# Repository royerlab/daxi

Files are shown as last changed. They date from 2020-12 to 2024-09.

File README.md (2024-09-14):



# DaXi: High-Resolution, Large Imaging Volume, and Multi-View Single Objective Light-Sheet Microscope

DaXi_blender_render

The DaXi microscope is a single-objective light-sheet microscope design that combines the advantages of standard single-objective microscopes with the speed, coverage, resolution, and gentleness of light-sheet microscopes. Its main features include a wider field of view and high-resolution imaging via a custom remote focusing objective, fast volumetric imaging over larger volumes without compromising image quality or necessitating tiled acquisition, fuller image coverage for large samples via multi-view imaging, and higher throughput multi-well imaging via remote coverslip placement. The microscope achieves a resolution of 450 nm laterally and 2 μm axially over an imaging volume of 3,000 × 800 × 300 μm, making it suitable for imaging large living samples such as developing embryos. The DaXi microscope also improves sample mounting ergonomics and can be converted from upright to inverted using remote focusing. The microscope has been successfully used to image various systems, including Drosophila egg chamber development, zebrafish whole-brain activity, and zebrafish embryonic development, up to nine embryos at a time.

DaXi has been published in Nature Methods in 2022:
[Yang, B., Lange, M., Millett-Sikking, A. et al. DaXi—high-resolution, large imaging volume and multi-view single-objective light-sheet microscopy. Nat Methods 19, 461–469 (2022).](https://doi.org/10.1038/s41592-022-01417-2)

Biorxiv preprint: https://doi.org/10.1101/2020.09.22.309229
Suplementary information for the paper can be found [here](https://www.biorxiv.org/content/10.1101/2020.09.22.309229v2.supplementary-material).  

This repository contains all CAD drawings, parts list, control software, and simulation for the microscope.
It is our goal to enable the community to build their own replicates of this system. Don't hesitate to post 
issues to this repo to request addtional information or report issues.  

Correspondence: loic.royer@czbiohub.org, bin.yang@czbiohub.org

## Contents

* [CAD models](https://github.com/royerlab/daxi/tree/master/cad_models): custom designed parts used to built the microscope. The STL files can be used directly 
for 3D printing.

* [Part list](https://github.com/royerlab/daxi/tree/master/part_list): a list of all the necessary parts used to built the microscope. 
A rough estimate of the cost of the microscope is about $130k.

* [Control code](https://github.com/royerlab/daxi/tree/master/control_code): to control the microscope. A Micro-Manager script to setup the data acquisition and 
a python module to programme a NI DAQ system to synchronize other devices during the acquisition. 
Micro-Manager is used to control the camera and the microscope stage. 
The NI DAQ system uses digital signal to switch the lasers on/off, and analog signals to set the angle of
the galvo mirrors and the position of the piezo actuators. 

* [Simulation code](https://github.com/royerlab/daxi/tree/master/simulation_code): used to generate the results in Supplementary Figures 7 and 9. 

## Image Processing

The image processing code required to go from DaXi's raw data to a fully processed timelapse or even video is found [here](https://github.com/royerlab/dexp).

## Software Requirements
Code is only tested on Windows 10 operating system, many hardware drivers only exist for windows...

Micro-Manager Version is 2.0-gamma.

Python version 3.7.

## Citation:

If you use the hardwar designs or software code, please cite us:

[High-Resolution, Large Imaging Volume, and Multi-View Single Objective Light-Sheet Microscopy](https://doi.org/10.1101/2020.09.22.309229)

Bin Yang1*, Merlin Lange, Alfred Millett-Sikking, Ahmet Can Solak, Shruthi Vijaykumar, Wanpeng Wang, 
Hirofumi Kobayashi, Matthew N Mccarroll, Lachlan W Whitehead, Reto P Fiolka, Thomas B. Kornberg, 
Andrew G York, Loic A. Royer*

Link to the Biorxiv preprint:  https://doi.org/10.1101/2020.09.22.309229

## License
This project is covered under the BSD 3-clause license.

Copyright © 2021. Chan Zuckerberg Biohub. All rights reserved.



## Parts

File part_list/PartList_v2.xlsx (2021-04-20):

 |  |  |  |  | Grand total | $130568.35 | Prices don’t include tax
Optics in Figure
Utility | Decription | Supplier | Part number | Unit Price | Quantity | Sub_total | Note
O1 | 1.0NA 20x water objective | Olympus | XLUMPLFLN 20XW | $7189.00 | 1 | $7189.00
O2 | 0.80NA 20x air objective | Olympus | UPLXAPO20X | $3075.00 | 1 | $3075.00
O3 | 1.0NA 20x Solid Immersion | Special Optics | Calico AMS 2.0 | $30000.00 | 1 | $30000.00 | Custom objective from Calico, price is estimated
Scanning and swtiching galvos | 20 mm Galvo mirror, 40 Degree Optical Angle, S4 mirror | Cambridge Instrument | 6SD12205 | $2567.00 | 3 | $7701.00 | see Miscellenous for galvo control | need custom mount
2-axes galvo | galvo to adjust incident angles of the light sheet | Cambridge Instrument | 6SD12056 | $6288.00 | 1 | $6288.00 | need custom mount to have true orthorgonal axes
Emission Filter | Single band filter | Chroma | ET525/50m | $325.00 | 1 | $325.00
Emission Filter | Single band filter | Chroma | ET610/75m | $325.00 | 1 | $325.00
Excitation Filter | Quad band filter | Chroma | 89402x | $550.00 | 1 | $550.00
Dichroic mirror | Quad band filter | Chroma | ZT405/488/561/640rpcv2-UF3 | $700.00 | 1 | $700.00
TL1-TL3 | Super wide tube lens | Olympus | SWTLU-C | $383.52 | 3 | $1150.56
TL4-TL6 components | Laser Scanning Tube Lens | Thorlabs | TTL200MP | $1379.17 | 3 | $4137.51
TL4-TL6 components | 2 inch achromatic lens | Thorlabs | AC508-750 | $112.54 | 2 | $225.08
TL4-TL6 components | 2 inch achromatic lens | Thorlabs | AC508-500 | $112.54 | 2 | $225.08
TL4-TL6 components | 2 inch achromatic lens | Thorlabs | AC508-750-A-ML | $148.25 | 2 | $296.50
TL7_alternative | Tube Lens, f = 200 mm, | Thorlabs | TTL200 | $496.70 | 1 | $496.70 | can be used to adjust final magnification
TL7_alternative | Tube Lens, f = 165 mm, | Thorlabs | TTL165A | $731.30 | 1 | $731.30 | can be used to adjust final magnification
TL7_alternative | Tube Lens, f = 100 mm | Thorlabs | TTL100A | $818.85 | 1 | $818.85 | can be used to adjust final magnification
CL1 | cylindrical lens 50 mm | Thorlabs | LJ1695RM-A | $109.29 | 1 | $109.29
CL2 and CL3 | cylindrical lens 200 mm | Thorlabs | LJ1653RM-A | $114.70 | 2 | $229.40
Fiber output | Protected Silver Reflective Collimator, 450 nm - 20 µm, Ø2 mm Beam, FC/APC | Thorlabs | RC02APCP01 | $966.34 | 1 | $966.34
Other major devices
Utility | Decription | Supplier | Part number | Unit Price | Quantity | Sub_total | Note
Piezo for O3 | Fast PIFOC® Piezo Nanofocusing Z-Drive, 100μm | Physik Instrumente | PD72Z1SAQ | $4946.00 | 1 | $4946.00 | Including the controller | not used in current setup yet
Laser | Stradus series module at 488nm, 50mW output with ~0.8 mm beam | Vortran | Stradus® 488 – 50 | $5240.00 | 1 | $5240.00
Laser | Stradus series module at 561nm, 50mW output with ~0.7 mm beam | Vortran | Stradus® 561 – 50 | $5364.00 | 1 | $5364.00
Data acquistion card | CompactDAQ chassis (8 slot USB) | National Instrument | cDAQ-9178 | $1443.00 | 1 | $1443.00
Data acquistion card | 4 Ch, +/-10 V, 16-Bit, 100 kS/s/ch, AO Module | National Instrument | NI 9263 DSUB | $564.00 | 2 | $1128.00
Data acquistion card | 8-Channel, 100 ns, TTL Digital Input/Output Module | National Instrument | NI 9401 | $341.00 | 1 | $341.00
Sample translation | MS-2000 FLAT-TOP XY AUTOMATED STAGE | ASI | MS-2000 | $12950.00 | 1 | $12950.00 | include controller and stage insert | Hindsight: need to include the scan-optimized option
Fiber input | FiberPort, FC/APC | Thorlabs | PAF2-A7A | $626.12 | 1 | $626.12
Miscellenous
Utility | Decription | Supplier | Part number | Unit Price | Quantity | Sub_total | Note
For galvos | HOOK-UP STRND 14AWG Wires for Galvo controller | Digikey | NA | $455.94 | 1 | $455.94
For galvos | SWITCHING POWER SUPPLIES | Astrodyne TDI | MK320S-24 | $83.11 | 6 | $498.66
Camera | ORCA-Flash4.0 V3 Digital | Hamamastu | C13440-20CU-KIT | $16500.00 | 1 | $16500.00
Camera | Interface Kit - Firebird Camlink Board and 2 ea SDR-SDR Caml | Hamamastu | CAMRA-1007-000-KIT | $2000.00 | 1 | $2000.00
Custom mounts
Utility | Decription | Supplier | Part number | Unit Price | Quantity | Sub_total | Note
For galvos | CambrigeGavloMount 2 axes, orthorgonal mount | Protolabs | NA | $842.90 | 1 | $842.90 | CAD file available
For O1 mount | ST1XY_PiezoAdapter_bottom | Protolabs | NA | $161.00 | 1 | $161.00 | CAD file available
For O1 mount | ST1XY_PiezoAdapter_top | Protolabs | NA | $155.76 | 1 | $155.76 | CAD file available
For O1 mount | XR25P_Piezo_adapter_bottom | Protolabs | NA | $171.94 | 1 | $171.94 | CAD file available
For O1 mount | XR25P_Piezo_adapter_top | Protolabs | NA | $174.00 | 1 | $174.00 | CAD file available
For galvos | 20mmGalvoMount - Part 1_v2, custom mount | Protolabs | NA | $335.45 | 3 | $1006.35 | CAD file available
For O1 water dispenser | Olympus1p00_20x - ObjectiveWaterDispenser | 3D-printed | NA | NA | 1 | NA | CAD file available
Thorlabs optomechanics
O1-O3 translation | Manual translation stages | Thorlabs | XR25P | $436.09 | 3 | $1308.27
O1 translation | Motorized translation stages | Thorlabs | ZFS25B (https://www.thorlabs.com/thorproduct.cfm?partnumber=ZFS25B) | $1250.92 | 1 | $1250.92
xy translation | XY Translator with Micrometer Drives | Thorlabs | ST1XY-S | $400.38 | 4 | $1601.52 | for objectives and fiberoutput
Mirror mount | Right-Angle Kinematic Mirror Mount | Thorlabs | KCB2C | $173.99 | 4 | $695.96
Mirror mount | Right-Angle Kinematic Mirror Mount | Thorlabs | KCB1C | $147.29 | 4 | $589.16
Mirror mount | Polaris® Ø2" Mirror Mount | Thorlabs | POLARIS-K2 | $293.25 | 3 | $879.75
Cage system | 60 mm Cage Plate, SM2 Threads | Thorlabs | LCP01 | $41.12 | 3 | $123.36
Alignment reference | PostMountable Standard Iris, Ø20.0 mm Max Aperture | Thorlabs | IDA20P5 | $223.78 | 1 | $223.78
Alignement check | Positive Combined Resolution and Distortion Test Target | Thorlabs | R1L1S1P | $520.05 | 1 | $520.05
Olympus tube lens adpator | Modified SM2-Threaded Mounting Adapter | Thorlabs | SM2AD-M41-SP | $120.00 | 3 | $360.00
Post | Ø1" Pedestal Pillar Post | Thorlabs | RS2P8E | $25.97 | 6 | $155.82
Post | Ø1" Post Holder with Flexure Lock, Pedestal Base | Thorlabs | RSH1.5 (https://www.thorlabs.com/thorproduct.cfm?partnumber=RSH1.5) | $33.28 | 2 | $66.56
Post | Ø1" Pillar Post | Thorlabs | RS1.5 | $23.27 | 2 | $46.54
Mirror mount | Compact Kinematic Mirror Mount Hex Adjuster | Thorlabs | KMSS | $37.87 | 3 | $113.61 | for dual view switch
Translation stage | Compact†25†mm†Travel†Linear†Translation†Stage | Thorlabs | XRN25C | $427.54 | 1 | $427.54 | for dual view switch
Translation stage | Baseplate†for†Stages†with†2¢†Wide†Dovetails | Thorlabs | XRNB1 | $32.62 | 1 | $32.62 | for dual view switch
Breadboard assembly | Aluminum Breadboard | Thorlabs | MB8 | $74.90 | 1 | $74.90 | parts to assemble the breadboard
Breadboard assembly | Aluminum Breadboard | Thorlabs | MB1218 | $187.83 | 1 | $187.83 | parts to assemble the breadboard
Breadboard assembly | Aluminum Breadboard | Thorlabs | MB618 | $129.11 | 1 | $129.11 | parts to assemble the breadboard
Breadboard assembly | Aluminum Breadboard | Thorlabs | MB1824 | $375.66 | 1 | $375.66 | parts to assemble the breadboard
Breadboard assembly | Aluminum Breadboard | Thorlabs | MB1836 | $568.64 | 1 | $568.64 | parts to assemble the breadboard
Breadboard assembly | Aluminum Breadboard | Thorlabs | MB810 | $115.16 | 1 | $115.16 | parts to assemble the breadboard
Breadboard assembly | Right≠Angle†Mounting†Plate | Thorlabs | AP90 | $83.71 | 3 | $251.13 | parts to assemble the breadboard
Breadboard assembly | Large Right-Angle Mounting Plate | Thorlabs | AP90L | $164.27 | 1 | $164.27 | parts to assemble the breadboard
Breadboard assembly | 18" Vertical Bracket for Breadboards | Thorlabs | VB01B | $129.11 | 3 | $387.33 | parts to assemble the breadboard
Dichroic mount | Kinematic†Fluorescence†Filter†Cube¨ | Thorlabs | DFM1L | $374.58 | 1 | $374.58

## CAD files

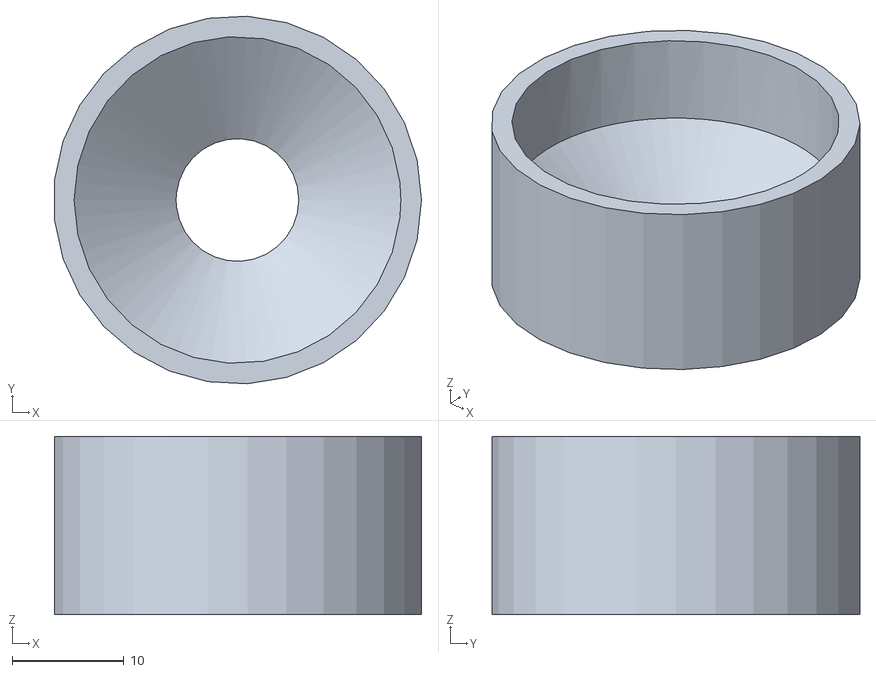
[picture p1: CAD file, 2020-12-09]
cad_models/Olympus1p00_20x - ObjectiveWaterDispenser.stl
32.9 x 33.0 x 16.0

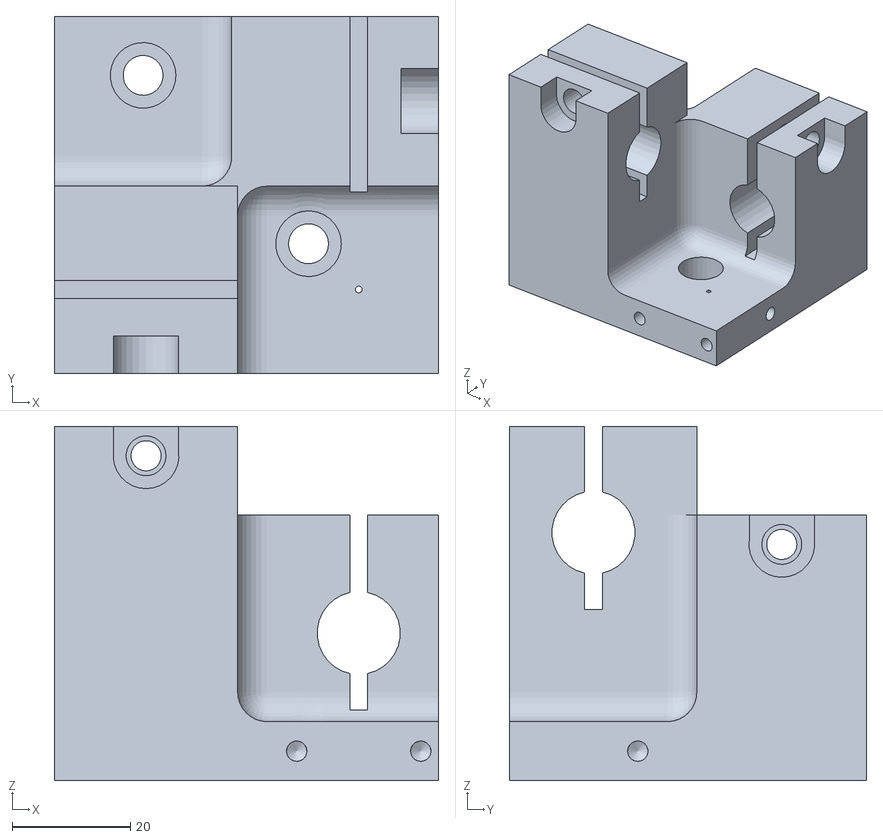
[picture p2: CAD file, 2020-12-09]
cad_models/2axes_CambridgeGavloMount - LeftHand.stl
65.0 x 60.5 x 60.0

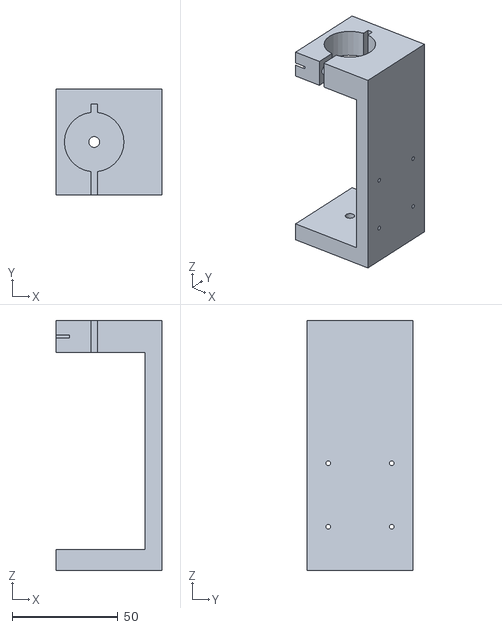
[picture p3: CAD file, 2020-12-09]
cad_models/20mmGalvoMount.stl
50.0 x 50.0 x 118.0

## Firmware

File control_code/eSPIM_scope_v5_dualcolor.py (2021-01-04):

"""making ao channel to send a sequence of signals"""
import nidaqmx
import nidaqmx.system
import numpy as np
import time


def set_dio_state(ch, value):
    """set a DIO channel,
    false to low, true to high"""
    with nidaqmx.Task() as task:
        task.do_channels.add_do_chan(ch)
        task.write([value], auto_start=True)


def set_ao_value(ch, value):
    """set the ao channel to value"""
    with nidaqmx.Task() as task:
        task.ao_channels.add_ao_voltage_chan(ch)
        task.write([value], auto_start=True)


class NIDaq:
    # Channel information
    ch_ao0 = "cDAQ1AO/ao0"  # scanning channel
    ch_ao1 = "cDAQ1AO/ao1"  # view switching
    ch_ao2 = "cDAQ1AO/ao2"  # view switching
    ch_ao3 = "cDAQ1AO/ao3"  # stripe reduction

    ch_ctr0 = "cDAQ1/_ctr0"  # for retrigger
    ch_ctr0_internal_output = "/cDAQ1/Ctr0InternalOutput"
    ch_ctr1 = "cDAQ1/_ctr1"  # for counting number of frames
    ch_ctr1_internal_output = "/cDAQ1/Ctr1InternalOutput"
    ch_ctr2 = "cDAQ1/_ctr2"  # idle
    ch_ctr3 = "cDAQ1/_ctr3"  # idle

    PFI0 = "/cDAQ1/PFI0"  # camera exposure input
    PFI1 = "/cDAQ1/PFI1"    # idle

    ch_dio0 = "cDAQ1DIO/port0/line0"  # 488 digital channel
    ch_dio1 = "cDAQ1DIO/port0/line1"  # 561 digital channel
    ch_dio2 = "cDAQ1DIO/port0/line2"  # bright field
    ch_dio3 = "cDAQ1DIO/port0/line3"  # idle
    ch_dio4 = "cDAQ1DIO/port0/line4"  # idle
    ch_dio5 = "cDAQ1DIO/port0/line5"  # idle
    ch_dio6 = "cDAQ1DIO/port0/line6"  # idle
    ch_dio7 = "cDAQ1DIO/port0/line7"  # idle

    # constants
    MAX_VOL = 10  # unit: v, maximum voltage of the ao channels
    MIN_VOL = -10  # unit: v, minimal voltage of the ao channels
    CONVERT_RATIO = 159  # unit: um / v, to convert from voltage to the scan distance of the galvo
    READOUT_TIME_FULL_CHIP = 0.01  # unit: second, the readout time of the full chip camera
    MAX_VERTICAL_PIXELS = 2048     # unit: pixels, maximal number of pixels along the vertical direction

    def __init__(
            self,
            exposure: float,
            nb_timepoints: int,
            scan_step: float,
            stage_scan_range: float,
            *,
            vertical_pixels: int = 2048,    # unit: pixels, number of pixels along the vertical direction
            num_samples: int = 20,  # for timing
            offset_view1: float  = 1550,   # unit: um, offset needed for view1
            offset_view2: float  = 1650,   # unit: um, offset needed for view2
            view1_galvo1: float  = 4.2,    # unit: v, to apply on galvo 1 for view 1
            view1_galvo2: float  = -4.08,  # unit: v, to apply on galvo 2 for view 1
            view2_galvo1: float  = -4.37,  # unit: v, to apply on galvo 1 for view 2
            view2_galvo2: float  = 3.66,   # unit: v, to apply on galvo 2 for view 2
            stripe_reduction_range: float = 0.1,    # unit: v, to apply on glavo gamma to reduce stripe
            stripe_reduction_offset: float = 0.58  # unit: v, to apply on glavo gamma to reduce stripe
        ):
        """
        Constructor of NIDaq.

        Parameters
        ----------
        exposure : float
            Expose time. Its unit is seconds.
        nb_timepoints : int
            Number of timepoints. Number of stacks to acquire.
        scan_step : float
            Scanning step size. unit: um.
        stage_scan_range : float
            Total range of stage scanning. unit: um.
        readout_time : float
             Readout time of the camera for full chip, unit: second.

        # TODO: add missing docstrings for rest of the optional arguments.
        """
        self.exposure = exposure
        self.nb_timepoints = nb_timepoints
        self.scan_step = scan_step
        self.stage_scan_range = stage_scan_range
        self.readout_time = self.READOUT_TIME_FULL_CHIP * vertical_pixels / self.MAX_VERTICAL_PIXELS
        self.num_samples = num_samples
        self.offset_view1 = offset_view1
        self.offset_view2 = offset_view2
        self.view1_galvo1 = view1_galvo1
        self.view1_galvo2 = view1_galvo2
        self.view2_galvo1 = view2_galvo1
        self.view2_galvo2 = view2_galvo2
        self.stripe_reduction_range = stripe_reduction_range
        self.stripe_reduction_offset = stripe_reduction_offset

        print("number of slices:", self.nb_slices)
        print("current sampling_rate is:", self.sampling_rate)

    @property
    def nb_slices(self):
        return int(self.stage_scan_range / self.scan_step) # for scanning, plus 2 due to Flash4 camera

    @property
    def sampling_rate(self):
        return self.num_samples / self.exposure

    def _get_ao_data(self, view: str):
        """generate the ndarray for an ao channel"""

        # for stripe reduction
        stripe_min = -self.stripe_reduction_range + self.stripe_reduction_offset
        stripe_max = self.stripe_reduction_range + self.stripe_reduction_offset
        nb_on_sample = round((self.exposure - self.readout_time) * self.sampling_rate)
        nb_off_sample = round(self.readout_time * self.sampling_rate)
        data_ao3 = list(np.linspace(stripe_min, stripe_max, nb_on_sample))
        data_ao3.extend([stripe_min] * nb_off_sample)

        # for view switching and light sheet stabilization
        if view == "view1":
            offset = self._offset_dis_to_vol(self.offset_view1)   # convert the offset from um to v
            min_range = - self.scan_step / 2 / self.CONVERT_RATIO
            max_range = self.scan_step / 2 / self.CONVERT_RATIO
            data_ao0 = list(np.linspace(max_range + offset, min_range + offset, self.num_samples))
            data_ao1 = [self.view1_galvo1] * self.num_samples
            data_ao2 = [self.view1_galvo2] * self.num_samples
            return [data_ao0, data_ao1, data_ao2, data_ao3]
        elif view == "view2":
            offset = self._offset_dis_to_vol(self.offset_view2)  # convert the offset from um to v
            min_range = - self.scan_step / 2 / self.CONVERT_RATIO
            max_range = self.scan_step / 2 / self.CONVERT_RATIO
            data_ao0 = list(np.linspace(max_range + offset, min_range + offset, self.num_samples))
            data_ao1 = [self.view2_galvo1] * self.num_samples
            data_ao2 = [self.view2_galvo2] * self.num_samples
            return [data_ao0, data_ao1, data_ao2, data_ao3]

    def _get_do_data(self, channels):
        """
        Method to get digital output data.
        """
        if len(channels) == 1:
            nb_on_sample = round((self.exposure - self.readout_time) * self.sampling_rate)
            data = [True] * nb_on_sample + [False] * (self.num_samples - nb_on_sample)
            return [data]
        elif len(channels) == 2:
            nb_on_sample = round((self.exposure - self.readout_time) * self.sampling_rate)
            nb_off_sample = round(self.readout_time * self.sampling_rate)
            data_on = [True] * nb_on_sample + [False] * (self.num_samples - nb_on_sample)
            data_off = [False] * self.num_samples
            # return [[data_on, data_off], [data_off, data_on]]
            return [data_on + data_off, data_off + data_on]
        else:
            raise ValueError('Only supported up to 2 channels for now')

    def _crate_ao_task_for_acquisition(self):
        """create ao task for acquisition, include all the needed ao channels"""
        task_ao = nidaqmx.Task("ao0")
        task_ao.ao_channels.add_ao_voltage_chan(self.ch_ao0)
        task_ao.ao_channels.add_ao_voltage_chan(self.ch_ao1)
        task_ao.ao_channels.add_ao_voltage_chan(self.ch_ao2)
        task_ao.ao_channels.add_ao_voltage_chan(self.ch_ao3)
        return task_ao

    def acquire_stacks(self, channels, view):
        """acquire stackes, depending on the given channel and view.
        view=0, first view only;
        view=1, second view only;
        view=2, both views;
        channel=[488], [561], or [488, 561]
        """
        task_ao = self._crate_ao_task_for_acquisition()
        task_do = nidaqmx.Task("do0")  # for laser control

        # slect channel
        if channels == [488]:
            task_do.do_channels.add_do_chan(self.ch_dio0)
        elif channels == [561]:
            task_do.do_channels.add_do_chan(self.ch_dio1)
        elif channels == [488, 561]:
            task_do.do_channels.add_do_chan(self.ch_dio0)
            task_do.do_channels.add_do_chan(self.ch_dio1)
        else:
            raise ValueError('Channel not supported')

        # slect view
        if view == 0:
            self._acquire_stacks(task_ao, task_do, channels, ["view1"])
        elif view == 1:
            self._acquire_stacks(task_ao, task_do, channels, ["view2"])
        elif view == 2:
            self._acquire_stacks(task_ao, task_do, channels, ["view1", "view2"])
        else:
            raise ValueError('View not supported')

        task_ao.close()
        task_do.close()

    def _acquire_stacks(self, task_ao, task_do, channels, views):
        """set up the workflow to acquire multiple stacks"""
        data_ao = [self._get_ao_data(v) for v in views]  # different for each view due to different offsets
        data_do = self._get_do_data(channels)    # get the digital output data depending on the channels

        # set up the counter for loop through a zstack
        task_ctr_loop = nidaqmx.Task("counter0")
        ctr_loop = task_ctr_loop.ci_channels.add_ci_count_edges_chan(self.ch_ctr1, edge=nidaqmx.constants.Edge.RISING)
        ctr_loop.ci_count_edges_term = self.PFI0

        # set up the counter to retrigger the ao and do channels
        task_ctr_retrig = nidaqmx.Task("counter1")
        task_ctr_retrig.co_channels.add_co_pulse_chan_freq(self.ch_ctr0,
                                                           idle_state=nidaqmx.constants.Level.LOW,
                                                           freq=self.sampling_rate)
        task_ctr_retrig.timing.cfg_implicit_timing(sample_mode=nidaqmx.constants.AcquisitionType.FINITE,
                                                   samps_per_chan=self.num_samples)
        task_ctr_retrig.triggers.start_trigger.cfg_dig_edge_start_trig(trigger_source=self.PFI0,
                                                                       trigger_edge=nidaqmx.constants.Slope.RISING)
        task_ctr_retrig.triggers.start_trigger.retriggerable = True

        # set up ao channel
        task_ao.timing.cfg_samp_clk_timing(rate=self.sampling_rate,
                                           source=self.ch_ctr0_internal_output,
                                           sample_mode=nidaqmx.constants.AcquisitionType.CONTINUOUS)

        task_ctr_retrig.start()
        for _ in range(self.nb_timepoints):
            for v in range(len(data_ao)):  # change view
                # print("ao data size: ", len(data_ao))
                # print("ao data size2: ", len(data_ao[v]))
                # print("ao data size3: ", len(data_ao[v][0]))
                task_ao.write(data_ao[v])
                task_ao.start()
                for i_ch in range(1): #range(len(channels)):  # change channel # run once
                    # set up the do channel
                    task_do.timing.cfg_samp_clk_timing(rate=self.sampling_rate,
                                                       source=self.ch_ctr0_internal_output,
                                                       sample_mode=nidaqmx.constants.AcquisitionType.CONTINUOUS)
                    task_do.write(data_do)
                    task_do.start()
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

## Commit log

2020-12-09 add part list and cad models
    [20mmGalvoMount.stl, 2axes_CambridgeGavloMount - LeftHand.stl, Olympus1p00_20x - ObjectiveWaterDispenser.stl, PartList_v2.xlsx]
2021-03-30 add simulation code, part list, cad models
    [20mmGalvoMount.stl, 2axes_CambridgeGavloMount - LeftHand.stl, Olympus1p00_20x - ObjectiveWaterDispenser.stl, PartList_v2.xlsx]
2021-04-12 update part list
    [PartList_v2.xlsx]
2021-04-20 update partlist and readme
    [PartList_v2.xlsx]
